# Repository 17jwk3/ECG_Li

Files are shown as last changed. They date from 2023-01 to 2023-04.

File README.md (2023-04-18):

# Real-time Wearable-based Cardiac Monitoring with Machine Learning
This project was part of ELEC490/498: Electrical Computer Engineering Capstone Project. A 3 semester long undertaking at Queen's Univeristy, Ontario, Canada. 

## Design Problem
Heart disease describes a range of conditions that affect a person’s heart, including blood vessel disease, arrhythmias, valve disease, etc.Various tests are used to diagnose heart conditions. Doctors start with a risk assessment looking into medical history, blood pressure, as well as past and current symptoms but further tests may be required. These methods can be hard to access for most people, due to socio-economic factors. This is a long and outdated process in the digital era of telemedicine. Doctors and patients need fast, easily accessible procedures. 

Many forms of it can be prevented with healthy lifestyle choices and medical interventions. Stress can affect the body mentally and physically left unchecked manifests as an increased heart rate among other symptoms contributing to high blood pressure, diabetes, and heart disease.

Computational advancements have increased the ability to concurrently predict and prevent cardiac abnormalities. Thus creating faster, less intrusive, and more easily accessible methods for patients and practitioners alike.

## Design and Implementaiton

Low-cost ECG (electrocardiogram) electrodes using a 3 lead configuraiton are used to capture impulses through the heart muscles and transmit the information via Bluetooth to a machine-learning algorithm in real-time to provide actionable feedback on potential abnormalities and stress levels via a Graphical User Interface, as seen in the following implementation pipeline.

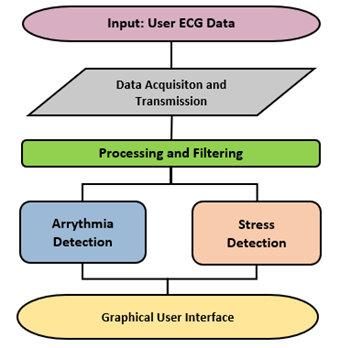
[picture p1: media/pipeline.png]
pipeline


---------------

### Hardware @17jwk3

The PCB uses a ESP32-C3-MINI-1-N4, a Li-Po with a battery charging module and a buck conmverter to supply 3.3V to the rest of the components. 
The main ECG components are an AD8232 opAmp board utilized for reading the electrical signals of the wearers heart and jack port for the 3 leads. 

#### PCB
This is a 4 layer PCB board that uses a AD8232 breakout board for the ECG pickup. 
The schematic, featuring over charge and discharge protection, switches to control: MCU power, 5V (charging) and Battery power. Also includes ESD protection for usb type C. The brains is an ESP32-C3-MINI-1-N4.

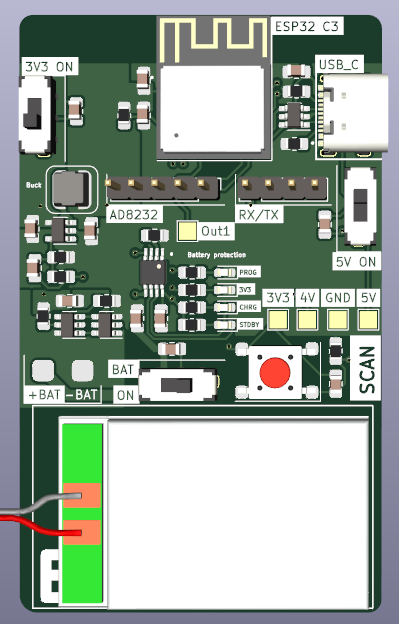
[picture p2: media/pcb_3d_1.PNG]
3D model

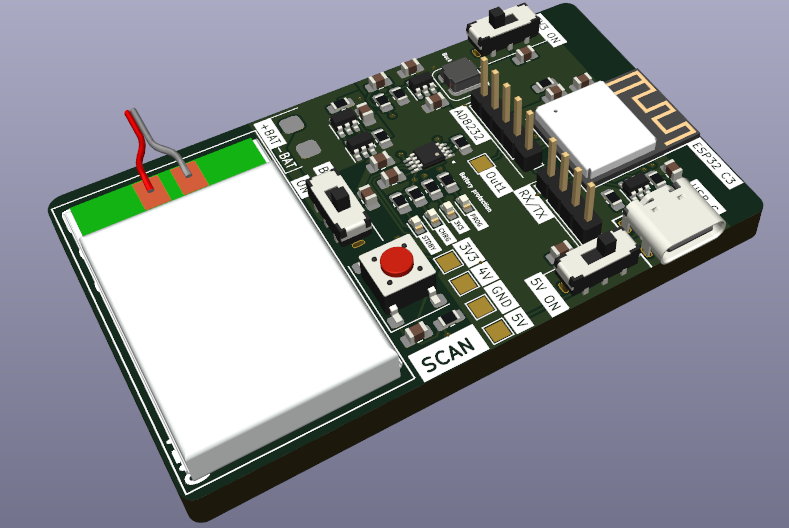
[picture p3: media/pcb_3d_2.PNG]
4 layers


#### PCB layout 
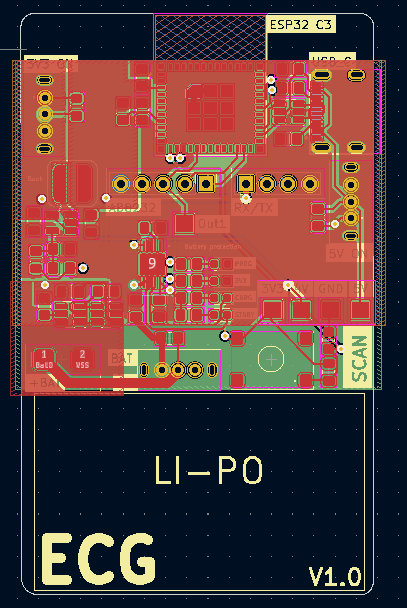
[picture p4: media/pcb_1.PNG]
Layer 1,2,3,4

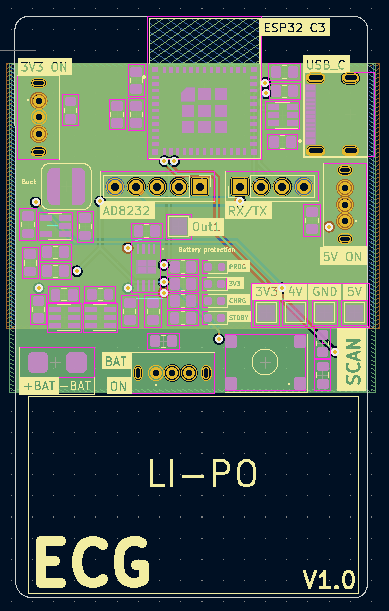
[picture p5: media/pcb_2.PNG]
Layer 2,3,4

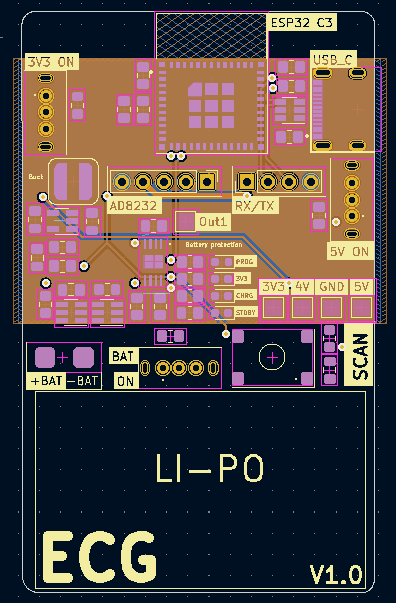
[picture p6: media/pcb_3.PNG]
Layer 3,4

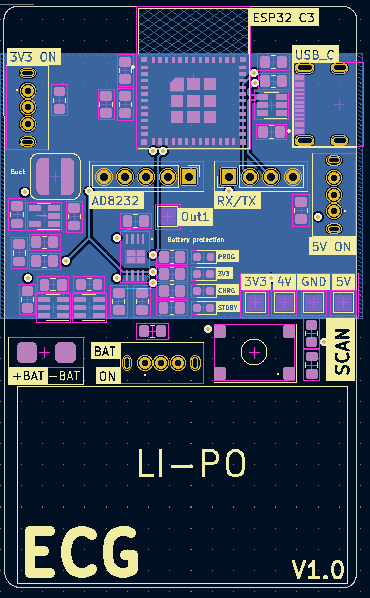
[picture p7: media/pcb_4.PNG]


#### Schematic
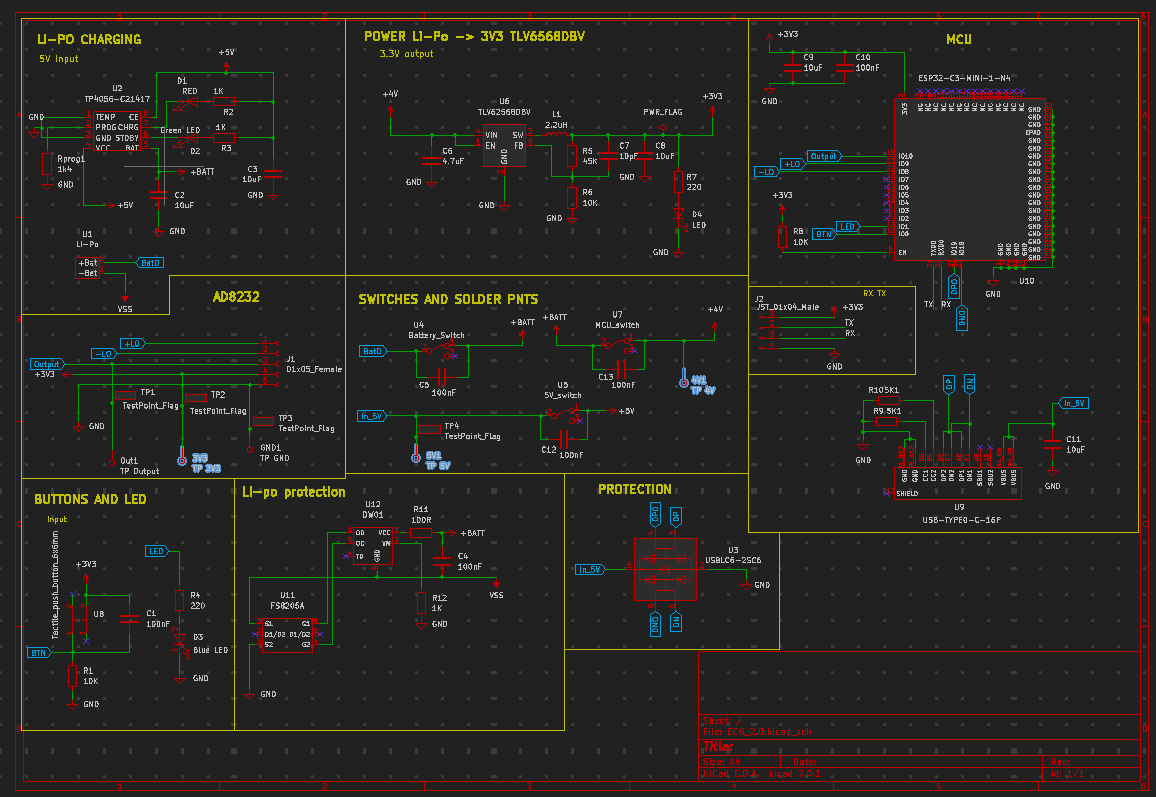
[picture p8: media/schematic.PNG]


#### Findings & Changes

The selected ESP32 module was a "standard" component for JLCPCB which means it costed much more to manufacture this board then originally anticipated. A chip that does not require "standard" assembly would be selected going forward. 

With more time, the AD8232 module would be integrated onto the board to increase portability with a very small lipo battery. Additional changes would be made to optimize the layout, add more LEDs for feedback etc. 

The output of the AD8232 may have needed to include a pulldown resistor. 

---------------

### Data Acquisition @17jwk3
#### Design
Data is acquired using the AD8323 amplifier and processed by the ESP32 microcontroller. The amplifier is connected to a 3-lead system placed on the end-user’s person. The top L and R leads are used for data acquisition, while the third and lower lead is the grounding lead.  

The data is sampled at 6 seconds with a 115,200 baud rate. It uses a fixed 360 frequency in accordance with the arrhythmia dataset. Heart beats are characterized by shape and frequency. Abnormalities distinguished by pace (Sinus Arrhythmia, Bradycardia, etc.) would incur informational loss or distortion from domain resampling .

The firmware was coded using the Arduino IDE, a variant of the C++ programming language. It records when both L and R leads sense an electrical signal, as to avoid null readings from not being applied.

In order to create the dataset locally, run 'Models and Prediction/reciever.py'.

#### Findings & Changes

Modification in limb electrode placement invokes changes in ECG wave amplitudes, which may alter the clinical limits of ECG normality detection. It was uncovered that leads placed no further than 12” apart yield the cleanest readings. 

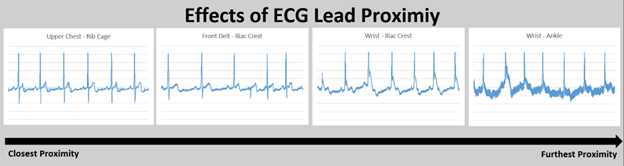
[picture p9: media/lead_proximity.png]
lead_proximity


---------------

### Processing and Filtering @CTy27
#### Design
Processing was designed to address missing values and noise artifacts from the raw ECG data using the appropriate filtering methods.

The constraints surrounding hardware filters far outweighed those using software, as hardware filters are more expensive, more difficult to test, and would increase the PCB footprint. Software filtering allows for greater control and optimization which leads to a more optimally processed resulting signal.

A technique known as imputation was used to recover lost values by synthesizing datapoints that hardware failed to capture. Particularly, K-Nearest Neighbors (KNN) imputation is a method used to impute missing values by finding the K closest observations and using their respective values to ‘fill in’ the missing ones. In the application of ECG processing, this method of imputation is beneficial as it accounts for the temporal structure of the data, making KNN imputation a natural choice.

The chosen implementation uses a 3rd order, lowpass Butterworth filter with a cutoff frequency of 50 Hz. 50Hz was found to be the optimal amount as observable high-frequency artifacts from power line interference and EMG were removed without limiting the low-frequency salient information. Lowering this cut-off frequency further resulted in distortion to the amplitude of the peaks, which would have adversely affected the prediction model’s performance. 

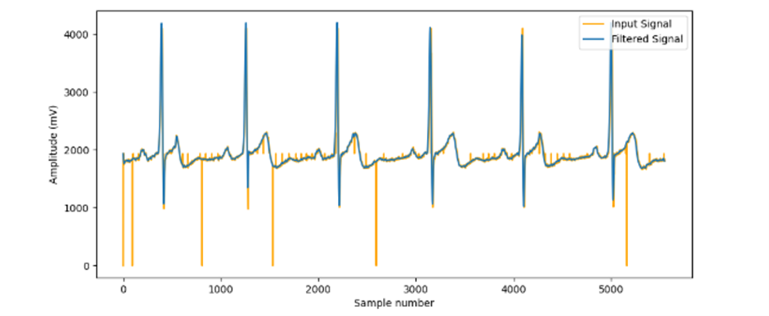
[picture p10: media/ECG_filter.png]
ECG_filter


#### Findings & Changes
Testing different filters and parameters was largely trial and error testing. Lowpass, high pass, bandpass, and notch filters were all tested, adjusting cut-off frequencies and passbands as appropriate. 

High pass and bandpass filters were susceptible to baseline wander, from samples 4,000 – 5,000 that the signal baseline drifts upwards. The high pass was also unable to filter out the high-frequency noise induced by Electromyography muscular activity (EMG), motion artifacts, and residual channel noise. The clear choice was lowpass as it maintains the salient, low-frequency information without distorting the signal with baseline wander. 

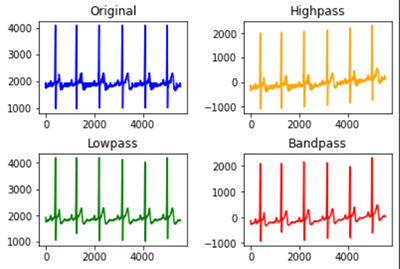
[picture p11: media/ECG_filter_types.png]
ECG_filter_types


There lies uncertainty in the exclusive use of lowpass to filter out noise, as a bandpass and a notch filter ensemble are standard for ECG data.  Solely relying on low-pass filters is not a common approach, however, the final product was sufficient for the classification models to perform adequately. 

---------------

### Arrhythmia Detection @alexkoch14
#### Design
The arrhythmia model was trained on the MIT-BIH database, containing 48-half-hour excerpts of two-channel ambulatory ECG recordings, obtained from 47 subjects studied by the BIH arrhythmia laboratory between 1975 and 1979.

The recordings were digitized at 360 samples per second and two or more cardiologists independently annotated each record.

The recordings were extracted using wfdb, the Python wave-form database package. ECG signals are transformed into snippets during the data pre-processing step as the model analyzes one-dimensional input data. 

Heartbeats in the first or last 3 seconds of the half-hour recording are ignored to reduce data clipping sizes, as is for any non-beat annotations. Beat symbols are encoded as abnormal (1) or normal (0). 

A sliding window of 6 seconds per beat segment is used to capture the current beat and those adjacent to retain enough information from encompassed patterns ensuring a 2-3 beat overlap. 
The following graph demonstrates that encoded abnormal beats (those other than ‘N’, later encoded to 1) yield an even distribution, thus eliminating the need for resampling. 

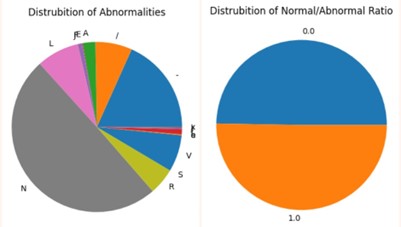
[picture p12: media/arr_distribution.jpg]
arr_distribution


Heartbeat voltages range among individuals depending on anatomy, body composition, blood volume, and ECG lead placement. Z-score normalization standardizes values into how much each reading deviates from the mean of all readings within the sample window.

In order to create the dataset locally, run 'Models and Prediction/arrhythmia_data.py'.

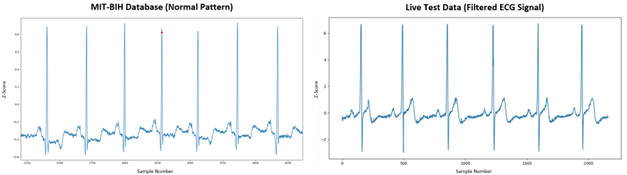
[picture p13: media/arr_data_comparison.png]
arr_data_comparison


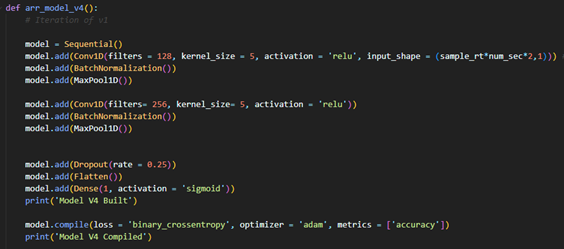
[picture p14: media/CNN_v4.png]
CNN


Leave-One-Out Crass-validation was employed via a hold-out set. The database was divided into three sets using a 60/30/10 train/validation/test split.
The holdout set primarily sought to encompass ~5 unseen subjects, consequentially representing ~10% of the data. 

The Deep-Learning (DL) model follows a Convolutional Neural Network architecture (CNN) using a TensorFlow backend.

arr_model_v4 uses a shallow, wide and simple architecture to overcome common real-time classification issues. 

The dataset has few features, but lots of records. This is perfect for DL models that need fewer parameters and sample complexity to achieve acceptable performance.

The model was trained on three passings of the training data (epochs). Accuracy decreased, loss increased, and overfitting began to occur beyond this point. 

In order to replicate the model, run 'Models and Prediction/arrhythmia_model.py'.

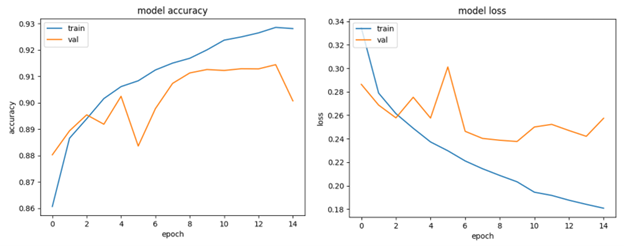
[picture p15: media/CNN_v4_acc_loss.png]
CNN_loss


#### Findings & Changes
arr_model_v4’s performance indicates 87.7% accuracy and 84% recall on the test set, which comprises unseen patients, as seen in 'media/CNN_v4_results.txt'.

This is satisfactory for real-time classification uses which aren’t meant to serve as a clinical diagnosis. 

It showed minimal signs of overfitting with training loss and validation losses of 0.2195 and 0.2264 respectively. 

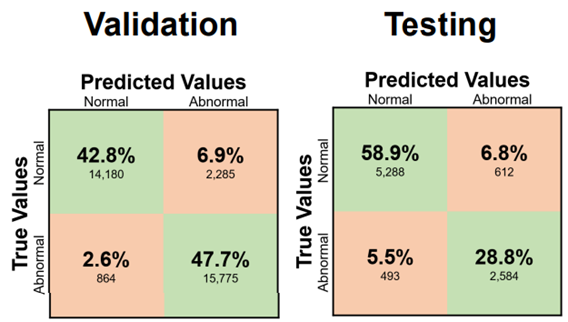
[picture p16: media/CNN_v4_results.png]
CNN_v4_results


A limitation of the current methodology lies in grouping all abnormal patterns to obtain even distribution without resampling. It is possible that CNN v4’s ~90% accuracy is accredited is predicting 80% of abnormality types with 100% accuracy, and the remaining 20% with 0% accuracy. The model might not be able to predict less prevalent abnormality patterns while being excellent in predicting common ones.

---------------

### Stress Detection @alexkoch14
#### Design
The multimodal SWELL Knowledge Work dataset for stress modeling (SWELL-KW) contains data from 25 participants (~3 hours each) performing typical office work (writing reports, reading emails, etc.) under 3 conditions: no stress (0), email interruptions (1) and time pressure (2).

The stress model was trained on HRV metrics obtained from the SWELL-KW dataset.
Inter-beat interval (IBI) samples are extracted from the raw ECG signal of each subject over the 3-hour time series. 
HRV indices are then computed on a subset of the IBI signal array. New samples are appended to the IBI array while the oldest is removed from the beginning,creating a sliding window of HRV indices over a fixed acquisition window analogous to the arrhythmia data. 
This facilitates a granular study of how momentary heartbeat patterns and concurrent HRV metrics reflect a subject’s stress level. 

HRV metrics are computed from the input filtered signal using hrv-analysis Python library.

Leave-One-Out Crass-validation was employed via a hold-out set. The database was divided into three sets using a 60/30/10 train/validation/test split.
The holdout set primarily sought to encompass ~3 unseen subjects, consequentially representing ~10% of the data. 

Twenty-three classification models were then assessed using the LazyPredict Python library, indicating Guassian Naive Bayes provides the best time/accuracy trade-off.

In order to replicate the model, run 'Models and Prediction/stress_model.py'.

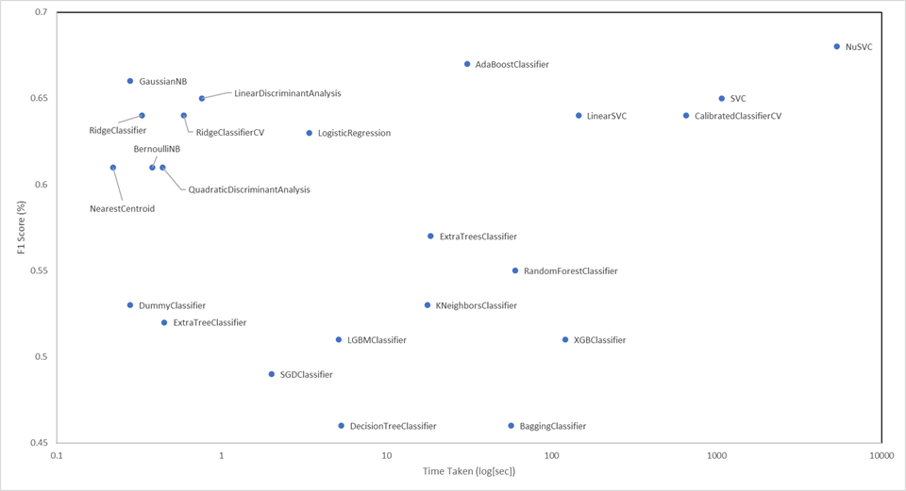
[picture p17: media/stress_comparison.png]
stress_comparison


#### Findings & Changes

Stress model performance indicates a 57.1% F1-score on the validaiton set and 67.6% F1-Score on the test set, as seen in media/stress_model_v5_results.txt

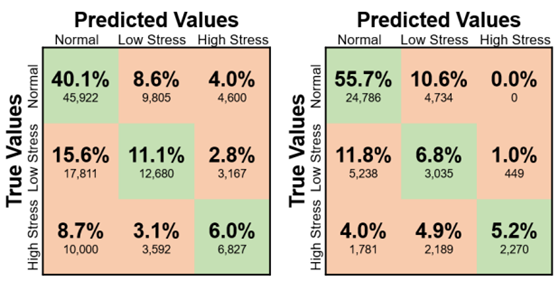
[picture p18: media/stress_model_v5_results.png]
stress_model_v5_results


The disparity in validation and testing sets accentuates some underlying points of issue. 

Models possess inherent predictive error which may lead to a relatively higher score on the test set due to chance.

The current neurobiological evidence suggests that HRV is impacted by stress and supports its use for an objective assessment of health, but it can be expressed through other psychological pathways (EDA, body posture, etc.).
These added features, which are not part of the feature set, are perhaps expressed more vividly in the validation subjects. 
Equivalently said, fewer people in the validation set tend to manifest stress predominantly through HRV than other physiological pathways. This is a limitation of training the stress model on a subset of a subset of the SWELL-KW dataset. 

Nonetheless, results are satisfactory for obtaining real-time assessments. Stress mitigation is a preventative step in cardiac abnormality evasion. It is the first line of defense, but an overpassed subject will get caught using CNN v4 used in arrhythmia detection.  

---------------

### Graphical User Interface @CTy27
#### Design
The GUI was designed to be responsive, have a low learning curve, and supply key metrics such as heart rate, abnormality likelihood, presence of stress, and supplement heart rate variability (HRV) metrics such as mean RR. These metrics were selected after conducting extensive research into clinical grade industry standard ECG monitors, to replicate their functionality.

The Python Tkinter library was selected to allow for seamless integration with the constituent sub-systems, as it can function using a single script requiring the end user to only use one file to access the functionality. Moreover, Tkinter is open sourced which ensures compatibility and facilitates future development. 

User testing was performed by gathering feedback from preliminary UI drafts. Users appreciated the color-coded feedback and unified design language, but feedback ultimately indicated that the lighter color scheme made the GUI appear less intimidating. 

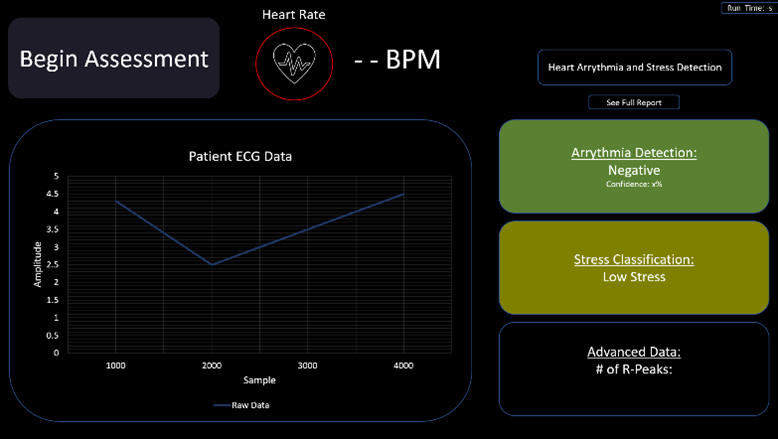
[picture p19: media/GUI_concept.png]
GUI_concept


The final design uses a clean modern interface with clear visualizations. It includes added features such as the ability to save and export data for further analysis via PDF using the “See Full Report” button. 

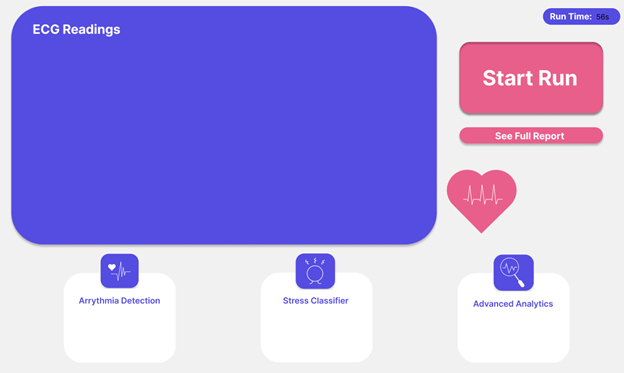
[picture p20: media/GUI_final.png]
GUI_final


#### Findings & Changes
The GUI acts as a proof of concept and does not store any medical data; it loses all information once the front end is closed and thus is not bound to any regulatory compliance. The information displayed is not a formal diagnosis and the documentation serves as a clear indicator of whether a medical professional should be consulted. 

It performs similarly to commercial products, allowing for user initiation of ECG readings, and those readings being displayed visually once complete. 

The largest weakness lies in the usage of Python. The Tkinter library is very limiting from a design perspective, making it difficult to implement a modern-looking dashboard. 
It only supports certain shapes, images, and colors which makes the overall appearance less customizable. 
Another weakness lies in the Tkinter structure which required all other sub-systems’ code to be embedded into a single file due. Restarting the entire program is therefore necessary to initiate a new run. 
This is inconvenient to the end user as this operation is computationally expensive and can add time to the entire experience. Using another Python library like PyQt, or a mobile app software like Swift would likely increase the overall user experience and allow for multiple runs without restarting the entire front end, but further research would need to be conducted. 

---------------

## Replication 

Clone the repositiry to you local machine and run:
'ECG_Li\Models and Prediction\gui.py'

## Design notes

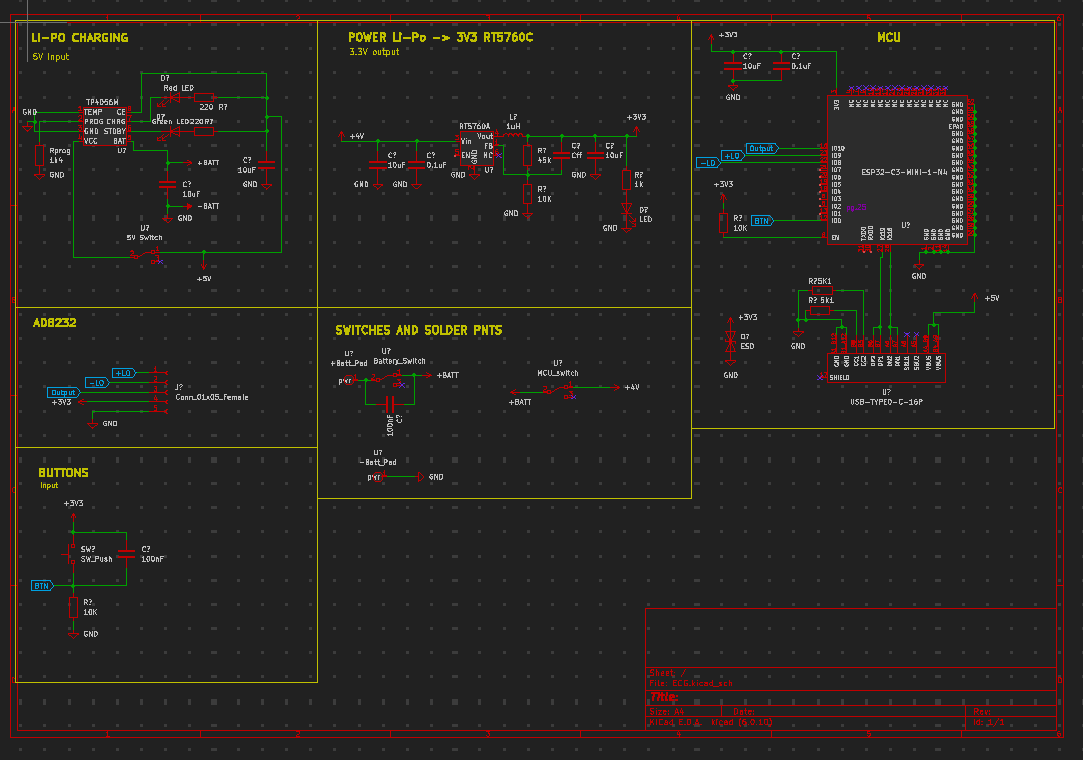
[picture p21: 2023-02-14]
media/schematic_dark.png

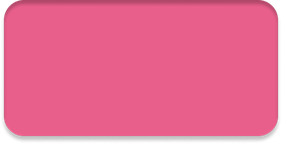
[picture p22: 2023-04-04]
Models and Prediction/assets/button_2.png

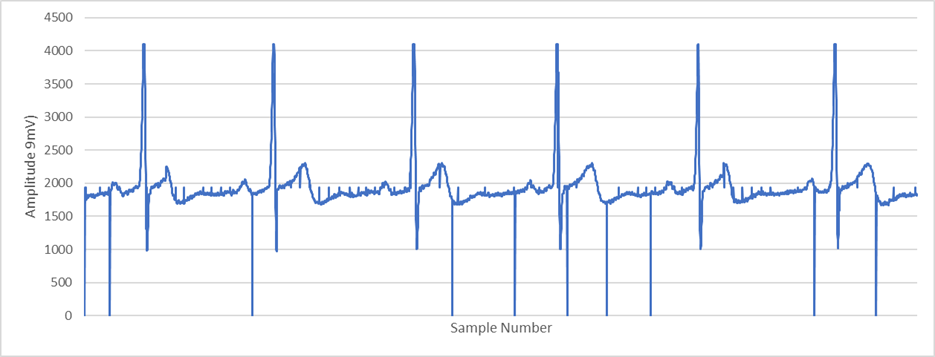
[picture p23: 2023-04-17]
media/Unfiltered ECG.png

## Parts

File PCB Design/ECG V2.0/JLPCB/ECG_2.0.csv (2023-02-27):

Comment | Designator | Footprint | JLCPCB Part#
100nF | C1, C4, C5, C10, C12, C13, | Capacitor_SMD:C_0805_2012Metric_Pad1.18x1.45mm_HandSolder | C38141
10uF | C2, C3, C8, C9, C11, | Capacitor_SMD:C_0805_2012Metric_Pad1.18x1.45mm_HandSolder | C1713
4.7uF | C6, | Capacitor_SMD:C_0805_2012Metric_Pad1.18x1.45mm_HandSolder | C412634
10pF | C7, | Capacitor_SMD:C_0805_2012Metric_Pad1.18x1.45mm_HandSolder | C157608
RED | D1, | LED_SMD:LED_0603_1608Metric | C84263
Green LED | D2, | LED_SMD:LED_0603_1608Metric | C434420
Blue LED | D3, | LED_SMD:LED_0603_1608Metric | C264469
LED | D4, | LED_SMD:LED_0603_1608Metric | C84265
JST_01x04_Male | J2, | Connector_PinHeader_2.54mm:PinHeader_1x04_P2.54mm_Vertical | C5116483
2.2uH | L1, | Inductor:CY43-2.2uH | C2929416
10K | R1, R6, R8, | Resistor_SMD:R_0805_2012Metric_Pad1.20x1.40mm_HandSolder | C17414
1K | R2, R3, R12, | Resistor_SMD:R_0805_2012Metric_Pad1.20x1.40mm_HandSolder | C17414
220 | R4, R7, | Resistor_SMD:R_0805_2012Metric_Pad1.20x1.40mm_HandSolder | C114742
45K | R5, | Resistor_SMD:R_0805_2012Metric_Pad1.20x1.40mm_HandSolder | C4310
5K1 | R9, R10, | Resistor_SMD:R_0805_2012Metric_Pad1.20x1.40mm_HandSolder | C115337
100R | R11, | Resistor_SMD:R_0805_2012Metric_Pad1.20x1.40mm_HandSolder | C115423
1k4 | Rprog1, | Resistor_SMD:R_0805_2012Metric_Pad1.20x1.40mm_HandSolder | C17388
TestPoint_Flag | TP1, TP2, TP3, TP4,
TP Output | TP5, | TestPoint:TestPoint_Pad_2.0x2.0mm
TP 3V3 | TP6, | TestPoint:TestPoint_Pad_2.0x2.0mm
TP GND | TP7, | TestPoint:TestPoint_Pad_2.0x2.0mm
TP 5V | TP8, | TestPoint:TestPoint_Pad_2.0x2.0mm
TP 4V | TP9, | TestPoint:TestPoint_Pad_2.0x2.0mm
Li-Po | U1, | Battery_solder_pads:Battery Solder Pad 2.5x2.0mm
TP4056-C21417 | U2, | Package_SO:MSOP-8-1EP_3x3mm_P0.65mm_EP2.5x3mm_Mask1.73x2.36mm | C21417
USBLC6-2SC6 | U3, | Package_TO_SOT_SMD:SOT-23-6 | C2827654
Battery_Switch | U4, | Switches:Battery_swt | C136719
5V_switch | U5, | Switches:5V | C136719
TLV62568DBV | U6, | Package_TO_SOT_SMD:SOT-23-5 | C163219
MCU_switch | U7, | Switches:3V3 SWT | C136719
Tactile_push_button_6x6mm | U8, | Buttons:Tactile_pushbutton_6x6mm | C273519
USB-TYPE0-C-16P | U9, | USBS:HRO_TYPE-C-31-M-12 | C709357
ESP32-C3-MINI-1-N4 | U10, | ESP32:XCVR_ESP32-C3-MINI-1-N4 | C2838502
FS8205A | U11, | Package_TO_SOT_SMD:SOT-23-6 | C908265
DW01 | U12, | Package_TO_SOT_SMD:SOT-23-6 | C181096

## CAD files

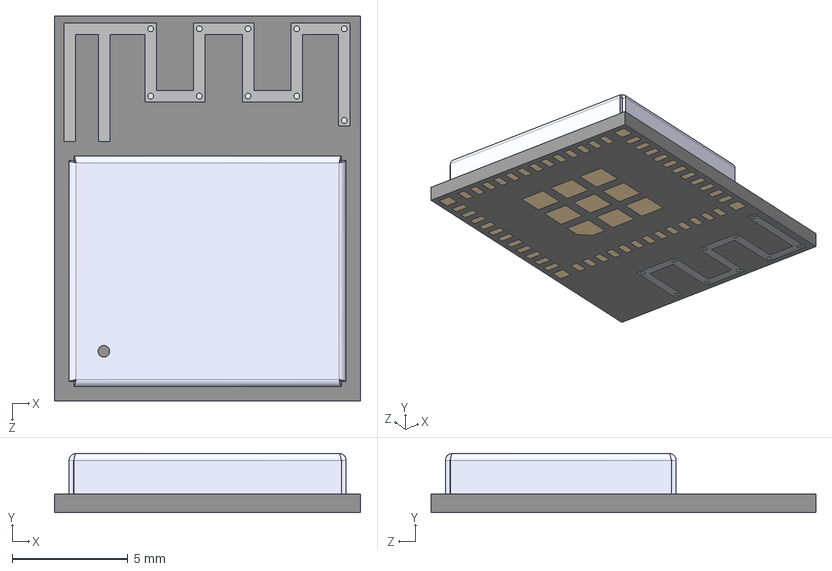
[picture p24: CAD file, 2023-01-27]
KiCad symbols and foorprints/ESP32-C3-MINI-1-N4/ESP32-C3-MINI-1-N4.step
13.2 x 2.55 x 16.6 mm

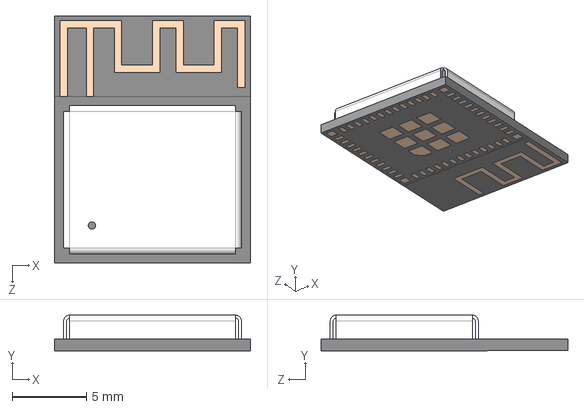
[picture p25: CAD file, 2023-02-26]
PCB Design/Models/ESP32-C3-MINI-1-N4/3D/ESP32-C3-MINI-1-N4.stp
13.2 x 2.40 x 16.6 mm

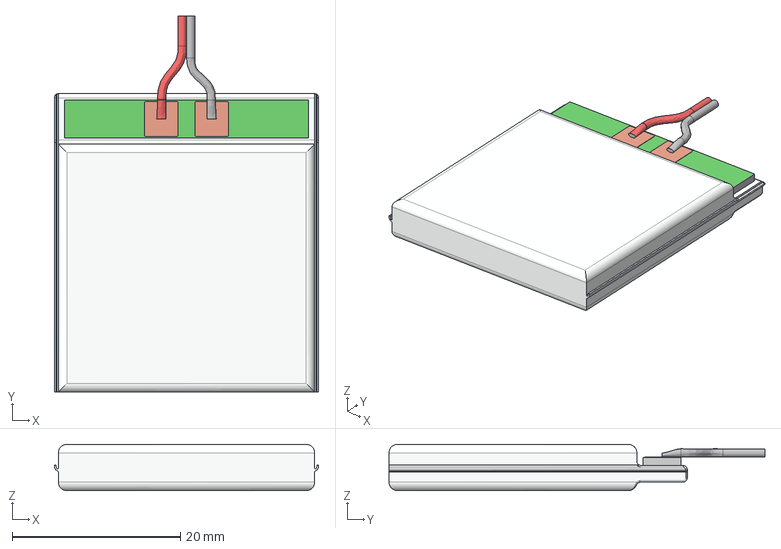
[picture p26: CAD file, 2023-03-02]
PCB Design/Models/Li-Po/LiPo battery 500 mAh.stp
31.4 x 44.8 x 5.50 mm

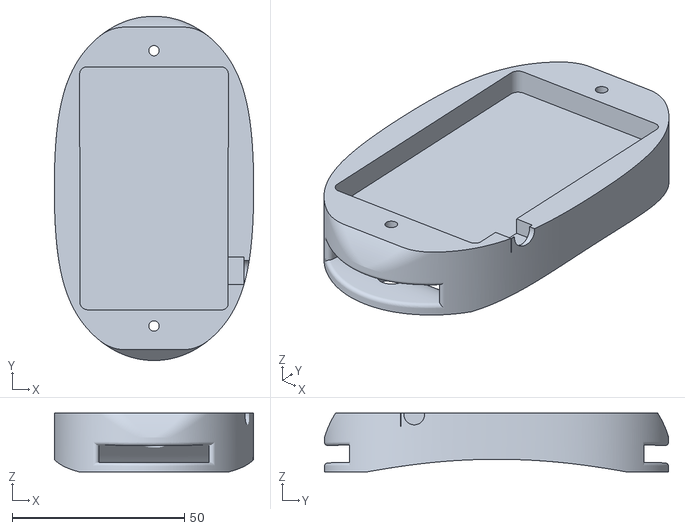
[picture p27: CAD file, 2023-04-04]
STLs/case_1of2.stl
57.9 x 99.9 x 17.0

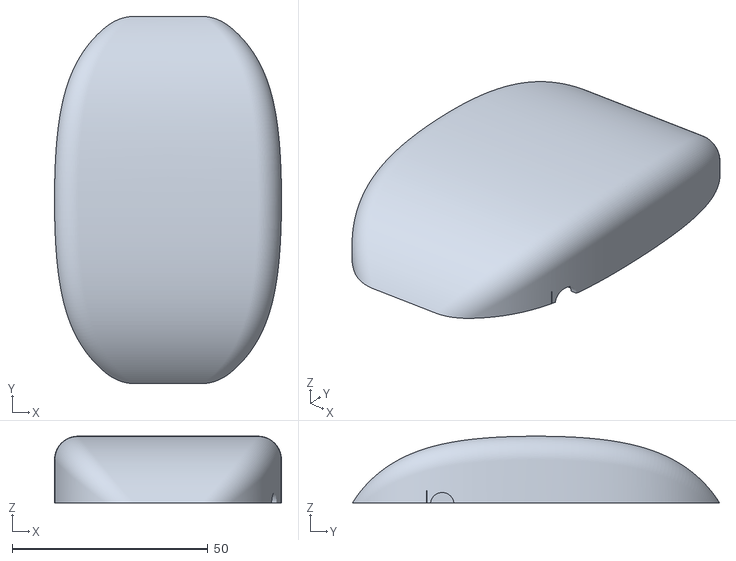
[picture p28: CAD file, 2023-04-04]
STLs/case_2of2.stl
57.9 x 93.7 x 17.0

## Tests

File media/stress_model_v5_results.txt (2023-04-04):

TEST SUBJECTS 23, 24
Model V5 Built
Model V5 Compiled
Model V5 Fitted
Training Prediction
Precision, Recall, F1 Score, Support
Note: Metrics calculated globally by counting the total true positives, false negatives and false positives
(0.5714592809788731, 0.5714592809788731, 0.5714592809788731, None)
Note: Metrics calculated for each label, and their average weight by support (the number of true instances for each label)
(0.5546344022000868, 0.5714592809788731, 0.5549714506458336, None)
Classification Report
              precision    recall  f1-score   support

           0      0.621     0.762     0.684    122553
           1      0.486     0.372     0.422     68563
           2      0.473     0.337     0.394     41478

    accuracy                          0.571    232594
   macro avg      0.527     0.491     0.500    232594
weighted avg      0.555     0.571     0.555    232594

Validation Prediction
Precision, Recall, F1 Score, Support
Note: Metrics calculated globally by counting the total true positives, false negatives and false positives
(0.5711230600024441, 0.5711230600024441, 0.5711230600024441, None)
Note: Metrics calculated for each label, and their average weight by support (the number of true instances for each label)
(0.5541479755335135, 0.5711230600024441, 0.5547976227668081, None)
Classification Report
              precision    recall  f1-score   support

           0      0.621     0.761     0.684     60327
           1      0.486     0.377     0.425     33658
           2      0.468     0.332     0.388     20577

    accuracy                          0.571    114562
   macro avg      0.525     0.490     0.499    114562
weighted avg      0.554     0.571     0.555    114562

Testing Prediction
Precision, Recall, F1 Score, Support
Note: Metrics calculated globally by counting the total true positives, false negatives and false positives
(0.6764758778831887, 0.6764758778831887, 0.6764758778831887, None)
Note: Metrics calculated for each label, and their average weight by support (the number of true instances for each label)
(0.6940588901005127, 0.6764758778831887, 0.6712554073048386, None)
Classification Report
              precision    recall  f1-score   support

           0      0.779     0.840     0.808     29520
           1      0.305     0.348     0.325      8722
           2      0.835     0.364     0.507      6240

    accuracy                          0.676     44482
   macro avg      0.640     0.517     0.547     44482
weighted avg      0.694     0.676     0.671     44482

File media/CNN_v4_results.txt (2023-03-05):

Model V4 Built
Model V4 Compiled
Model: "sequential"
_________________________________________________________________
 Layer (type)                Output Shape              Param #   
=================================================================
 conv1d (Conv1D)             (None, 2156, 128)         768       

 batch_normalization (BatchN  (None, 2156, 128)        512       
 ormalization)

 max_pooling1d (MaxPooling1D  (None, 1078, 128)        0
 )

 conv1d_1 (Conv1D)           (None, 1074, 256)         164096

 batch_normalization_1 (Batc  (None, 1074, 256)        1024
 hNormalization)

 max_pooling1d_1 (MaxPooling  (None, 537, 256)         0
 1D)

 dropout (Dropout)           (None, 537, 256)          0

 flatten (Flatten)           (None, 137472)            0

 dense (Dense)               (None, 1)                 137473

=================================================================
Total params: 303,873
Trainable params: 303,105
Non-trainable params: 768
_________________________________________________________________
None
Epoch 1/3
2101/2101 [==============================] - 2719s 1s/step - loss: 1.6784 - accuracy: 0.8333 - val_loss: 1.2448 - val_accuracy: 0.8092
Epoch 2/3
2101/2101 [==============================] - 2157s 1s/step - loss: 0.4378 - accuracy: 0.8880 - val_loss: 0.3312 - val_accuracy: 0.8909
Epoch 3/3
2101/2101 [==============================] - 2448s 1s/step - loss: 0.2195 - accuracy: 0.9180 - val_loss: 0.2264 - val_accuracy: 0.9049
Model V4 Fitted
WARNING:absl:Found untraced functions such as _jit_compiled_convolution_op, _jit_compiled_convolution_op, _update_step_xla while saving (showing 3 of 3). These functions will not be 
directly callable after loading.
Model V1 Saved
Training Predict
2101/2101 [==============================] - 485s 230ms/step
Accuracy:0.917
Recall:0.959
Precision:0.885

Validation Predict
1035/1035 [==============================] - 276s 267ms/step
Accuracy:0.905
Recall:0.948
Precision:0.873

Testing Predict
281/281 [==============================] - 73s 261ms/step
Accuracy:0.877
Recall:0.840
Precision:0.809

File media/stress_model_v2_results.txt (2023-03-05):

TEST SUBJECTS 23, 24
Model V2 Built
Model V2 Compiled
Model V2 Fitted
Training Prediction
              precision    recall  f1-score   support

           0      1.000     1.000     1.000    122521
           1      1.000     1.000     1.000    122713
           2      1.000     1.000     1.000    122354

    accuracy                          1.000    367588
   macro avg      1.000     1.000     1.000    367588
weighted avg      1.000     1.000     1.000    367588

Validation Prediction
              precision    recall  f1-score   support

           0      1.000     1.000     1.000     60359
           1      1.000     1.000     1.000     60167
           2      1.000     1.000     1.000     60526

    accuracy                          1.000    181052
   macro avg      1.000     1.000     1.000    181052
weighted avg      1.000     1.000     1.000    181052

Testing Prediction
              precision    recall  f1-score   support

           0      0.328     0.689     0.445     29520
           1      0.221     0.100     0.137     29520
           2      0.323     0.144     0.200     29520

    accuracy                          0.311     88560
   macro avg      0.291     0.311     0.261     88560
weighted avg      0.291     0.311     0.261     88560

TEST SUBJECTS 1, 2
Model V2 Built
Model V2 Compiled
Model V2 Fitted
Training Prediction
              precision    recall  f1-score   support

           0      1.000     1.000     1.000    128783
           1      1.000     1.000     1.000    128563
           2      1.000     1.000     1.000    129056

    accuracy                          1.000    386402
   macro avg      1.000     1.000     1.000    386402
weighted avg      1.000     1.000     1.000    386402

Validation Prediction
              precision    recall  f1-score   support

           0      1.000     1.000     1.000     63457
           1      1.000     1.000     1.000     63677
           2      1.000     1.000     1.000     63184

    accuracy                          1.000    190318
   macro avg      1.000     1.000     1.000    190318
weighted avg      1.000     1.000     1.000    190318

Testing Prediction
              precision    recall  f1-score   support

           0      0.376     0.396     0.386     20160
           1      0.285     0.164     0.208     20160
           2      0.429     0.590     0.497     20160

    accuracy                          0.383     60480
   macro avg      0.364     0.383     0.364     60480
weighted avg      0.364     0.383     0.364     60480

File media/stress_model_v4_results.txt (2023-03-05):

TEST SUBJECTS 23, 24
Model V4 Built
Model V4 Compiled
Model V4 Fitted
Training Prediction
              precision    recall  f1-score   support

           0      0.459     0.526     0.490    122521
           1      0.571     0.420     0.484    122713
           2      0.572     0.641     0.604    122354

    accuracy                          0.529    367588
   macro avg      0.534     0.529     0.526    367588
weighted avg      0.534     0.529     0.526    367588

Validation Prediction
              precision    recall  f1-score   support

           0      0.458     0.524     0.489     60359
           1      0.567     0.417     0.481     60167
           2      0.571     0.639     0.603     60526

    accuracy                          0.527    181052
   macro avg      0.532     0.527     0.524    181052
weighted avg      0.532     0.527     0.524    181052

Testing Prediction
              precision    recall  f1-score   support

           0      0.554     0.897     0.685     29520
           1      0.122     0.039     0.060     29520
           2      0.723     0.763     0.743     29520

    accuracy                          0.567     88560
   macro avg      0.466     0.567     0.496     88560
weighted avg      0.466     0.567     0.496     88560

TEST SUBJECTS 1, 2
Model V4 Built
Model V4 Compiled
Model V4 Fitted
Training Prediction
              precision    recall  f1-score   support

           0      0.493     0.586     0.535    128783
           1      0.526     0.344     0.416    128563
           2      0.599     0.692     0.642    129056

    accuracy                          0.541    386402
   macro avg      0.539     0.541     0.531    386402
weighted avg      0.539     0.541     0.531    386402

Validation Prediction
              precision    recall  f1-score   support

           0      0.493     0.585     0.535     63457
           1      0.528     0.347     0.419     63677
           2      0.597     0.691     0.641     63184

    accuracy                          0.541    190318
   macro avg      0.539     0.541     0.532    190318
weighted avg      0.539     0.541     0.531    190318

Testing Prediction
              precision    recall  f1-score   support

           0      0.516     0.512     0.514     20160
           1      1.000     0.374     0.545     20160
           2      0.534     0.871     0.662     20160

    accuracy                          0.586     60480
   macro avg      0.683     0.586     0.574     60480
weighted avg      0.683     0.586     0.574     60480

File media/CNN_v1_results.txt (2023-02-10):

Model V1 Built
Model V1 Compiled
Model: "sequential"
_________________________________________________________________
 Layer (type)                Output Shape              Param #   
=================================================================
 conv1d (Conv1D)             (None, 2156, 128)         768       

 dropout (Dropout)           (None, 2156, 128)         0

 flatten (Flatten)           (None, 275968)            0

 dense (Dense)               (None, 1)                 275969    

=================================================================
Total params: 276,737
Trainable params: 276,737
Non-trainable params: 0
_________________________________________________________________
None
Epoch 1/15
2101/2101 [==============================] - 610s 286ms/step - loss: 0.3346 - accuracy: 0.8606 - val_loss: 0.2864 - val_accuracy: 0.8803
Epoch 2/15
2101/2101 [==============================] - 550s 262ms/step - loss: 0.2789 - accuracy: 0.8865 - val_loss: 0.2687 - val_accuracy: 0.8893
Epoch 3/15
2101/2101 [==============================] - 551s 262ms/step - loss: 0.2614 - accuracy: 0.8939 - val_loss: 0.2578 - val_accuracy: 0.8954
Epoch 4/15
2101/2101 [==============================] - 520s 248ms/step - loss: 0.2490 - accuracy: 0.9016 - val_loss: 0.2754 - val_accuracy: 0.8919
Epoch 5/15
2101/2101 [==============================] - 507s 241ms/step - loss: 0.2373 - accuracy: 0.9061 - val_loss: 0.2577 - val_accuracy: 0.9025
Epoch 6/15
2101/2101 [==============================] - 499s 237ms/step - loss: 0.2298 - accuracy: 0.9083 - val_loss: 0.3012 - val_accuracy: 0.8836
Epoch 7/15
2101/2101 [==============================] - 499s 237ms/step - loss: 0.2212 - accuracy: 0.9124 - val_loss: 0.2464 - val_accuracy: 0.8978
Epoch 8/15
2101/2101 [==============================] - 499s 238ms/step - loss: 0.2145 - accuracy: 0.9150 - val_loss: 0.2404 - val_accuracy: 0.9074
Epoch 9/15
2101/2101 [==============================] - 498s 237ms/step - loss: 0.2088 - accuracy: 0.9169 - val_loss: 0.2388 - val_accuracy: 0.9113
Epoch 10/15
2101/2101 [==============================] - 509s 242ms/step - loss: 0.2034 - accuracy: 0.9201 - val_loss: 0.2377 - val_accuracy: 0.9126
Epoch 11/15
2101/2101 [==============================] - 506s 241ms/step - loss: 0.1945 - accuracy: 0.9237 - val_loss: 0.2500 - val_accuracy: 0.9122
Epoch 12/15
2101/2101 [==============================] - 509s 242ms/step - loss: 0.1918 - accuracy: 0.9250 - val_loss: 0.2523 - val_accuracy: 0.9129
Epoch 13/15
2101/2101 [==============================] - 510s 243ms/step - loss: 0.1877 - accuracy: 0.9265 - val_loss: 0.2470 - val_accuracy: 0.9129
Epoch 14/15
2101/2101 [==============================] - 513s 244ms/step - loss: 0.1842 - accuracy: 0.9286 - val_loss: 0.2421 - val_accuracy: 0.9145
Epoch 15/15
2101/2101 [==============================] - 565s 269ms/step - loss: 0.1809 - accuracy: 0.9281 - val_loss: 0.2575 - val_accuracy: 0.9007
Model V1 Fitted
Training Predict
2101/2101 [==============================] - 63s 30ms/step
Accuracy:0.932
Recall:0.958
Precision:0.912

Validation Predict
1035/1035 [==============================] - 40s 38ms/step
Accuracy:0.901
Recall:0.925
Precision:0.883

Testing Predict
281/281 [==============================] - 8s 30ms/step
Accuracy:0.878
Recall:0.834
Precision:0.814

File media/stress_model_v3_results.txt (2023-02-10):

Model V3 Built
Model V3 Compiled
Model V3 Fitted
Training Prediction
              precision    recall  f1-score   support

           0      0.725     0.733     0.729     41695
           1      0.725     0.757     0.741     41546
           2      0.753     0.711     0.731     41489

    accuracy                          0.734    124730
   macro avg      0.734     0.734     0.734    124730
weighted avg      0.734     0.734     0.734    124730

Validation Prediction
              precision    recall  f1-score   support

           0      0.725     0.723     0.724     20360
           1      0.723     0.760     0.741     20509
           2      0.749     0.713     0.731     20566

    accuracy                          0.732     61435
   macro avg      0.732     0.732     0.732     61435
weighted avg      0.732     0.732     0.732     61435

Testing Prediction
              precision    recall  f1-score   support

           0      0.748     0.672     0.707     29520
           1      0.230     0.341     0.275      8722
           2      0.609     0.489     0.543      6240

    accuracy                          0.581     44482
   macro avg      0.529     0.501     0.508     44482
weighted avg      0.627     0.581     0.599     44482

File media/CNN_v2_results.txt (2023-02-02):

Model V2 Compiled
Model: "sequential"
_________________________________________________________________
 Layer (type)                Output Shape              Param #   
=================================================================
 conv1d (Conv1D)             (None, 2158, 64)          256       

 elu (ELU)                   (None, 2158, 64)          0

 batch_normalization (BatchN  (None, 2158, 64)         256       
 ormalization)

 conv1d_1 (Conv1D)           (None, 2156, 64)          12352     

 elu_1 (ELU)                 (None, 2156, 64)          0

 batch_normalization_1 (Batc  (None, 2156, 64)         256
 hNormalization)

 max_pooling1d (MaxPooling1D  (None, 1078, 64)         0
 )

 conv1d_2 (Conv1D)           (None, 1076, 128)         24704

 elu_2 (ELU)                 (None, 1076, 128)         0

 batch_normalization_2 (Batc  (None, 1076, 128)        512       
 hNormalization)

 conv1d_3 (Conv1D)           (None, 1074, 128)         49280

 elu_3 (ELU)                 (None, 1074, 128)         0

 batch_normalization_3 (Batc  (None, 1074, 128)        512
 hNormalization)

 max_pooling1d_1 (MaxPooling  (None, 537, 128)         0
 1D)

 conv1d_4 (Conv1D)           (None, 535, 256)          98560     

 elu_4 (ELU)                 (None, 535, 256)          0

 batch_normalization_4 (Batc  (None, 535, 256)         1024
 hNormalization)

 conv1d_5 (Conv1D)           (None, 533, 256)          196864

 elu_5 (ELU)                 (None, 533, 256)          0

 batch_normalization_5 (Batc  (None, 533, 256)         1024
 hNormalization)

 max_pooling1d_2 (MaxPooling  (None, 266, 256)         0
 1D)

 flatten (Flatten)           (None, 68096)             0

 dense (Dense)               (None, 2048)              139462656

 elu_6 (ELU)                 (None, 2048)              0

 batch_normalization_6 (Batc  (None, 2048)             8192
 hNormalization)

 dropout (Dropout)           (None, 2048)              0

 dense_1 (Dense)             (None, 1)                 2049

=================================================================
Total params: 139,858,497
Trainable params: 139,852,609
Non-trainable params: 5,888
_________________________________________________________________
None
Epoch 1/2
2289/2289 [==============================] - 8600s 4s/step - loss: 0.3009 - accuracy: 0.4913
Epoch 2/2
2289/2289 [==============================] - 8516s 4s/step - loss: 0.1754 - accuracy: 0.4913
Model V2 Fitted
WARNING:absl:Found untraced functions such as _jit_compiled_convolution_op, _jit_compiled_convolution_op, _jit_compiled_convolution_op, _jit_compiled_convolution_op, _jit_compiled_convolution_op while saving (showing 5 of 7). These functions will not be directly callable after loading.
Model V2 Saved
2289/2289 [==============================] - 1144s 499ms/step
1128/1128 [==============================] - 591s 524ms/step
Model Predict
Train
AUC:0.500
Accuracy:0.491
Recall:1.000
Precision:0.491
Specificity:0.000
Prevalence:0.491

Valid
AUC:0.500
Accuracy:0.486
Recall:1.000
Precision:0.486
Specificity:0.000
Prevalence:0.486

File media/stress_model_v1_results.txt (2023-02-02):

Model: "sequential"
_________________________________________________________________
 Layer (type)                Output Shape              Param #
=================================================================
 dense (Dense)               (None, 16)                272

 dense_1 (Dense)             (None, 12)                204

 dense_2 (Dense)             (None, 3)                 39

=================================================================
Total params: 515
Trainable params: 515
Non-trainable params: 0
_________________________________________________________________
None
Training Predict
8200/8200 [==============================] - 36s 4ms/step
Accuracy:0.660
Recall:0.628
Precision:0.653
 
Validation Predict
4039/4039 [==============================] - 12s 3ms/step
Accuracy:0.660
Recall:0.629
Precision:0.653

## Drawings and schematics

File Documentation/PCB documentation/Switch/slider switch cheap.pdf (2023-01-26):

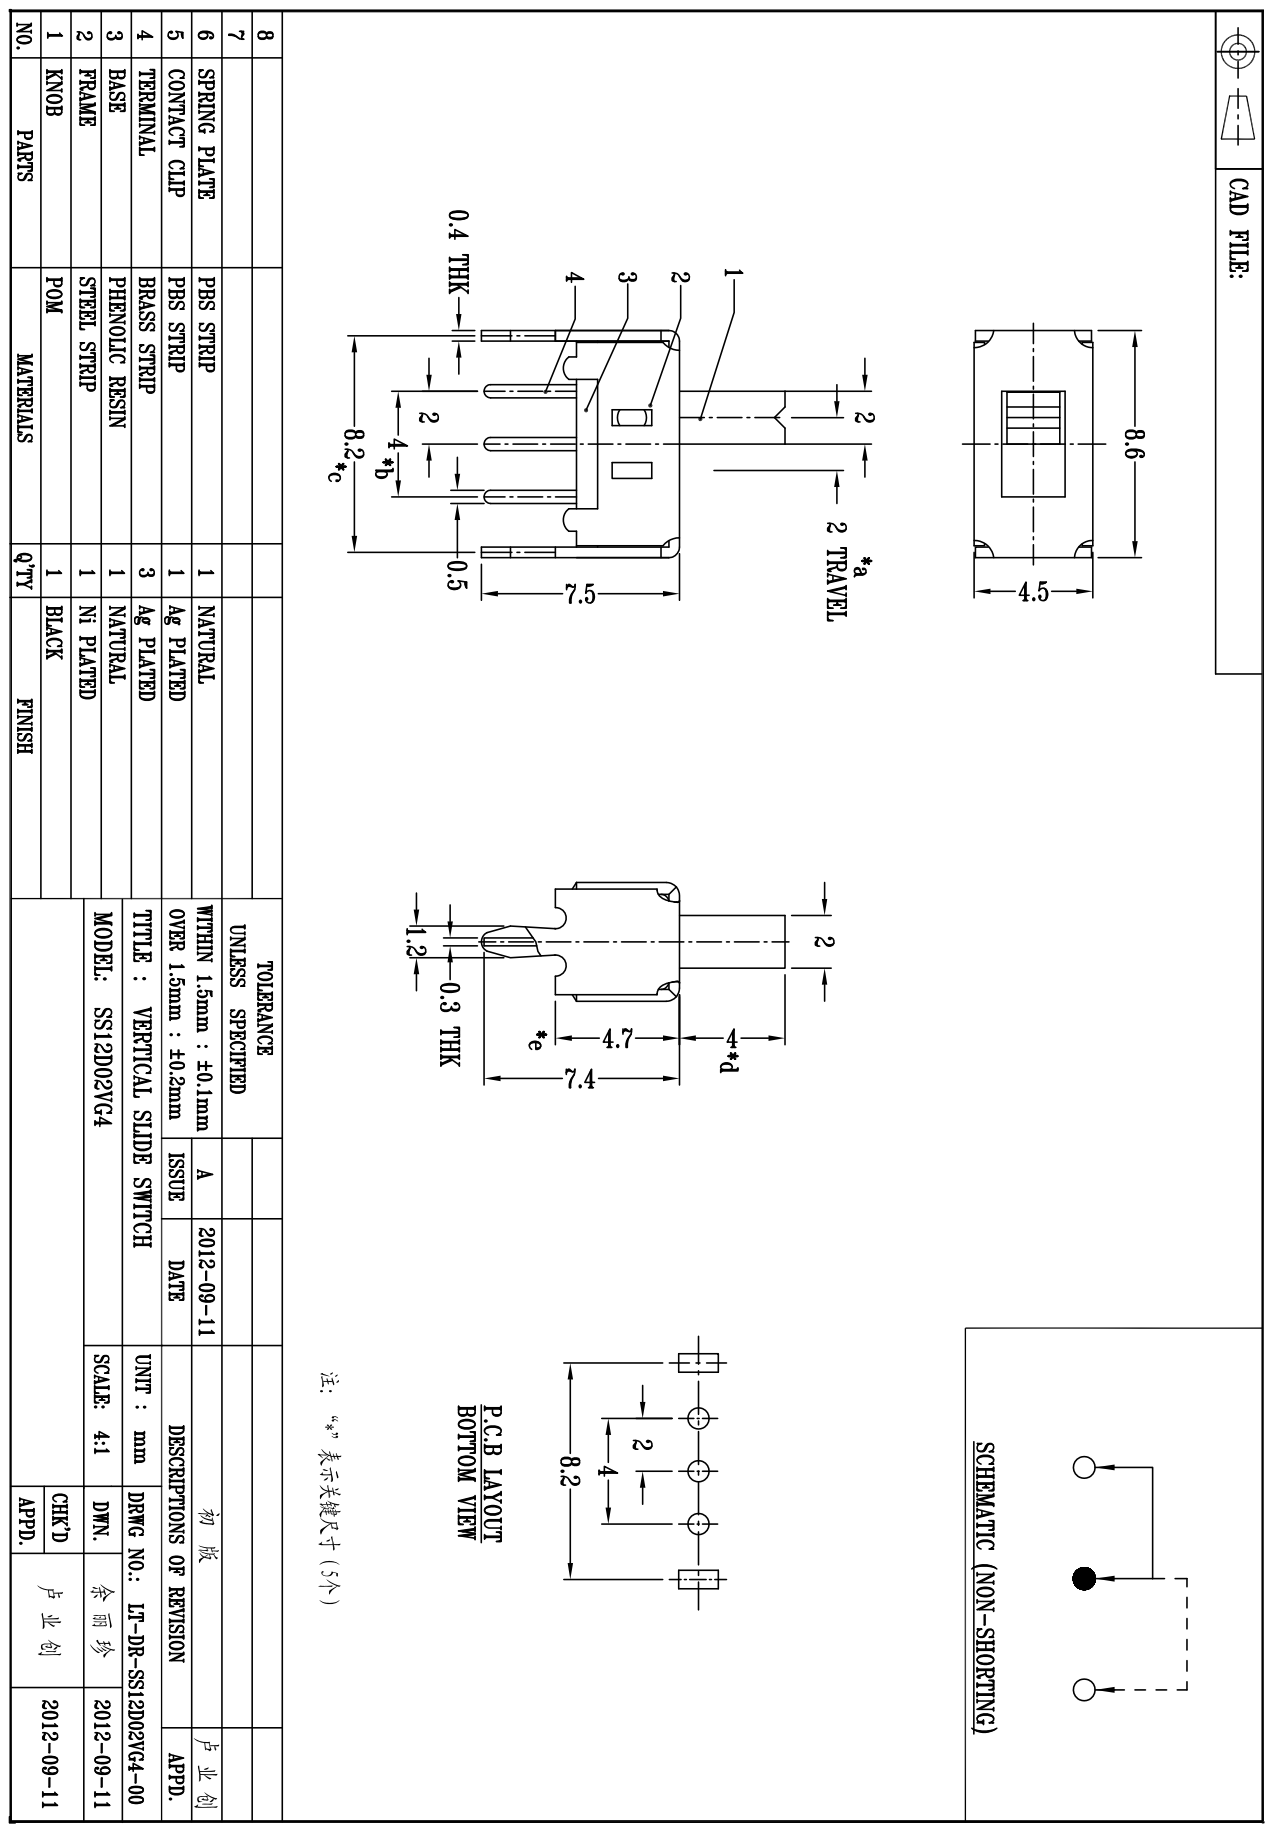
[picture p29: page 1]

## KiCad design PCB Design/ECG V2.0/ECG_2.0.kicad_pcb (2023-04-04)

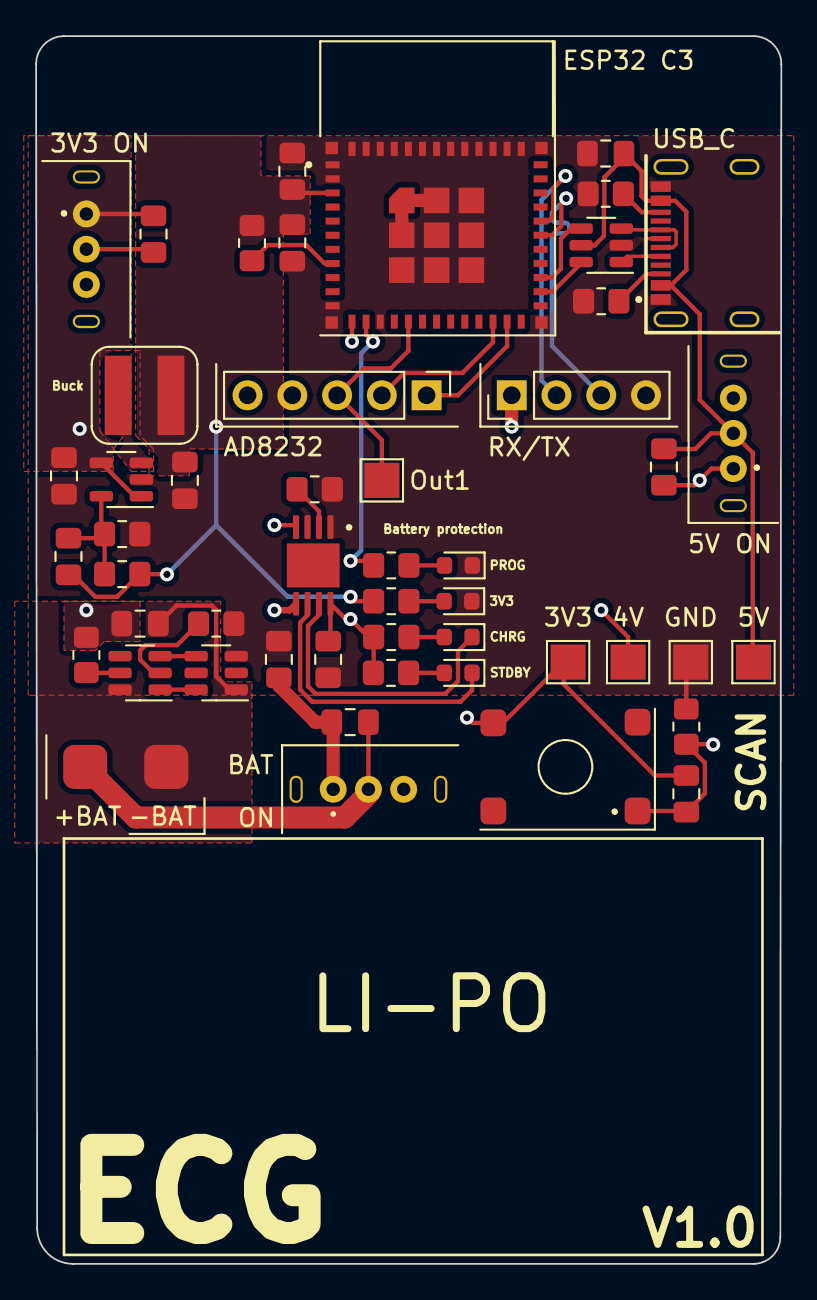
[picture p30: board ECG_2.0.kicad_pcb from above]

Board: 4 copper layers, 42.3 x 69.7 mm, 50 parts (0 on the bottom side), 35 nets.

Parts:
3V3: TP 3V3; TestPoint_Pad_2.0x2.0mm
4V: TP 4V; TestPoint_Pad_2.0x2.0mm
5V: TP 5V; TestPoint_Pad_2.0x2.0mm
C1, C4, C5, C10, C12, C13: 100nF; C_0805_2012Metric_Pad1.18x1.45mm_HandSolder
C2, C3, C8, C9, C11: 10uF; C_0805_2012Metric_Pad1.18x1.45mm_HandSolder
C6: 4.7uF; C_0805_2012Metric_Pad1.18x1.45mm_HandSolder
C7: 10pF; C_0805_2012Metric_Pad1.18x1.45mm_HandSolder
D1: RED; LED_0603_1608Metric
D2: Green LED; LED_0603_1608Metric
D3: Blue LED; LED_0603_1608Metric
D4: LED; LED_0603_1608Metric
GND: TP GND; TestPoint_Pad_2.0x2.0mm
J1: 01x05_Female; PinHeader_1x05_P2.54mm_Vertical
J2: JST_01x04_Male; PinHeader_1x04_P2.54mm_Vertical
L1: 2.2uH; CY43-2.2uH
Out1: TP Output; TestPoint_Pad_2.0x2.0mm
R1, R6, R8: 10K; R_0805_2012Metric_Pad1.20x1.40mm_HandSolder
R2, R3, R12: 1K; R_0805_2012Metric_Pad1.20x1.40mm_HandSolder
R4, R7: 220; R_0805_2012Metric_Pad1.20x1.40mm_HandSolder
R5: 45K; R_0805_2012Metric_Pad1.20x1.40mm_HandSolder
R9, R10: 5K1; R_0805_2012Metric_Pad1.20x1.40mm_HandSolder
R11: 100R; R_0805_2012Metric_Pad1.20x1.40mm_HandSolder
Rprog1: 1k4; R_0805_2012Metric_Pad1.20x1.40mm_HandSolder
U1: Li-Po; Battery Solder Pad 2.5x2.0mm
U2: TP4056-C21417; MSOP-8-1EP_3x3mm_P0.65mm_EP2.5x3mm_Mask1.73x2.36mm
U3: USBLC6-2SC6; SOT-23-6
U4: Battery_Switch; Battery_swt
U5: 5V_switch; 5V
U6: TLV62568DBV; SOT-23-5
U7: MCU_switch; 3V3 SWT
U8: Tactile_push_button_6x6mm; Tactile_pushbutton_6x6mm
U9: USB-TYPE0-C-16P; HRO_TYPE-C-31-M-12
U10: ESP32-C3-MINI-1-N4; XCVR_ESP32-C3-MINI-1-N4
U11: FS8205A; SOT-23-6
U12: DW01; SOT-23-6

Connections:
+3V3: 3V3.1, C1.1, C7.1, C8.1, C9.1, C10.1, J1.4, J2.1, L1.2, R5.1, R7.1, R8.1, U8.4, U10.3 (3V3)
+4V: 4V.1, C6.1, C13.1, U6.1 (EN), U6.4 (VIN), U7.1
+5V: C3.1, C12.1, R2.2, R3.2, U2.4 (VCC), U2.8 (CE), U5.1
+BATT: C2.1, C4.1, C5.1, C13.2, R11.2, U2.5 (BAT), U4.1, U7.2
+LO: J1.1, U10.23 (IO9)
-LO: J1.2, U10.22 (IO8)
/RX: J2.3, U10.30 (RXD0)
/TX: J2.2, U10.31 (TXD0)
BTN: C1.2, R1.1, U8.1, U10.12 (IO0)
BatO: C5.2, U1.1 (+Bat), U4.2
DN: U3.1 (I/O1), U9.A7 (DN1), U9.B7 (DN2)
DNO: U3.6 (I/O1), U10.26 (IO18)
DP: U3.3 (I/O2), U9.A6 (DP1), U9.B6 (DP2)
DPO: U3.4 (I/O2), U10.27 (IO19)
GND: C2.2, C3.2, C6.2, C8.2, C9.2, C10.2, C11.2, D3.1 (K), D4.1 (K), GND.1, J1.5, J2.4, R1.2, R6.2, R9.2, R10.2, R12.1, Rprog1.2, U2.1 (TEMP), U2.3 (GND), U3.2 (GND), U6.2 (GND), U9.A1_B12 (GND), U9.B1_A12 (GND), U10.1 (GND), U10.2 (GND), U10.11 (GND), U10.14 (GND), U10.36 (GND), U10.37 (GND), U10.38 (GND), U10.39 (GND), U10.40 (GND), U10.41 (GND), U10.42 (GND), U10.43 (GND), U10.44 (GND), U10.45 (GND), U10.46 (GND), U10.47 (GND), U10.48 (GND), U10.49 (EPAD), U10.50 (GND), U10.51 (GND), U10.52 (GND), U10.53 (GND), U11.3 (S2)
In_5V: 5V.1, C11.1, C12.2, U3.5 (VBUS), U5.2, U9.A4_B9 (VBUS), U9.B4_A9 (VBUS)
LED: R4.1, U10.13 (IO1)
unnamed: D1.2 (A), R2.1
unnamed: D1.1 (K), U2.7 (CHRG)
unnamed: D2.2 (A), R3.1
unnamed: D2.1 (K), U2.6 (STDBY)
unnamed: D3.2 (A), R4.2
unnamed: D4.2 (A), R7.2
unnamed: Rprog1.1, U2.2 (PROG)
unnamed: C7.2, R5.2, R6.1, U6.5 (FB)
unnamed: L1.1, U6.3 (SW)
unnamed: R9.1, U9.B8 (CC1)
unnamed: R10.1, U9.B5 (CC2)
unnamed: R8.2, U10.8 (EN)
unnamed: U11.6 (G1), U12.1 (OD)
unnamed: U11.4 (G2), U12.3 (OC)
unnamed: R11.1, U12.5 (VCC)
unnamed: R12.2, U12.2 (VM)
Output: J1.3, Out1.1, U10.16 (IO10)
VSS: C4.2, U1.2 (-Bat), U11.1 (S1), U12.6 (GND)

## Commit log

2023-01-26 Initial setup
    to new beginnings, your welcome.
    [ECG.kicad_pcb, ECG.kicad_sch]
2023-01-26 Continued work
    added buck converter and switch footprint
    [ECG.kicad_sch]
2023-01-27 Updates to schematic
    Correct and added MCU
    [ECG.kicad_sch]
2023-01-27 added sources files
    [ESP32-C3-MINI-1-N4.step]
2023-02-02 changes to pcb, added ad8232
    [ECG.kicad_sch]
2023-02-02 Prediction Models
    [ECG-Test-2.csv, stress metrics available.xlsx]
2023-02-05 Added user samples and receiver file
    [Shoulders and stomach 2.csv, Shoulders stomach.csv, Wrist and stomach 2.csv, Wrist and stomach Alex.csv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]
2023-02-06 updating ECG placement test results
    [COMPARISON.xlsx, Front Delt - Iliac Crest 2.csv, Front Delt - Iliac Crest.csv, Shoulders and stomach 2.csv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]
2023-02-06 update notes
    [stress metrics available.xlsx]
2023-02-07 changes to schematic of pcb
    [ECG.kicad_sch]
2023-02-10 Performance results
    Performance results of arr and stress models.
    [stress metrics available.xlsx]
2023-02-10 schem done, pcb 50%
    [AD8232.kicad_pcb, AD8232.kicad_sch, ECG.csv, ECG.kicad_pcb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]
2023-02-14 second last iteration hopefully
    pcb design, pending Bruno approval
    [ECG.kicad_pcb]
2023-02-26 Final PCB changes
    [AD8232.kicad_pcb, AD8232.kicad_sch, ECG.kicad_pcb, ecg try 2.csv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]
2023-02-26 Deleted old corrupt files
    [AD8232.kicad_pcb, AD8232.kicad_sch, ECG.kicad_pcb, ECG.kicad_sch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]
2023-02-26 readMe and media updates
    [ESP32-C3-MINI-1-N4.SchLib, ESP32-C3-MINI-1-N4.stp, ESP32C3MINI1N4.PcbLib, chips.prt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]
2023-02-26 BOM edits
    [ECG_2.0.csv, ECG_2.0.kicad_pcb]
2023-02-27 Gerber files and Larger pcb due to manufacturing limits
    [ECG_2.0-B_Cu.gbr, ECG_2.0-B_Mask.gbr, ECG_2.0-B_Paste.gbr, ECG_2.0-B_Silkscreen.gbr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]
2023-02-28 Final pcb
    [ECG_2.0-B_Cu.gbr, ECG_2.0-B_Mask.gbr, ECG_2.0-B_Paste.gbr, ECG_2.0-B_Silkscreen.gbr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]
2023-02-28 media changes
    [ECG_2.0-B_Cu.gbr, ECG_2.0-B_Mask.gbr, ECG_2.0-B_Paste.gbr, ECG_2.0-B_Silkscreen.gbr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]
2023-02-28 small updates to pcb
2023-03-02 added li-po and esp32 to models
    [ECG_2.0.kicad_pcb, LiPo battery 500 mAh.stp]
2023-03-05 New CNN model
    [Upper Chest - Rib Cage Dropped Values.csv]
2023-03-06 Implemented a new stress prediction model
    [stress model comparison.xlsx]
2023-03-14 Improved PCB design and Improved renderings
    [ECG_2.0.kicad_pcb]
2023-03-17 connections issue on pcb deisgn
    [ECG_2.0.kicad_pcb]
2023-03-22 Final GUI implementaiton
    [COMPARISON.xlsx, stress model comparison.xlsx]
2023-03-23 Showcase code changes
    [run time.xlsx]
2023-04-04 updated Schematic to reflect hardware testing issues
    Changed schematic for USB-C, had the pin our wrong.
    Changed through hole switch components and USB-C through hole for better fit.
    [ECG_2.0.kicad_pcb, ECG_2.0.kicad_sch, case_1of2.stl, case_2of2.stl]
2023-04-17 Cleaning up the directories
    [run time.xlsx, stress metrics available.xlsx, stress model comparison.xlsx]
